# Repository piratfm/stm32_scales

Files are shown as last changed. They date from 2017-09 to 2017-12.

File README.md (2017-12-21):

# STM32 scales

Software and hardware for child weight meter (scales) with glass LCD display
Based on branded Chicco weight meter model # 8312.60.001

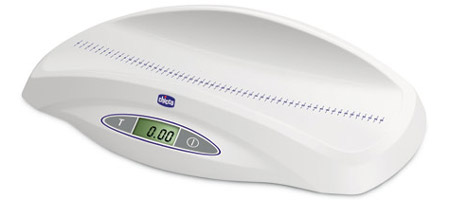
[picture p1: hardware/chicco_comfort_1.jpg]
scales image


Due original "brains" PCB became broken for some reason (operational amplifier burned-out, and scales always shows zeroes), the decision to replace
it by STM32 is made. As additional "pro", scales precision has been 10x increased, comparing to original "brains" of scales.

## Original parts that been used:
 * load sensors bridge (3 pins each).
 * original 5 symbol glass LCD display.
 * original plastic enclosure with pushbuttons.

## Used hardware:
 * HX711 ADC
 * STM32F103C8T6 as MCU and software-base LCD controller (by using RTC interrupts)
 
 schematic of the board: [schematic](https://github.com/piratfm/stm32_scales/blob/master/hardware/weightmeter_schematic.pdf)

## To calibrate:
 1. Put weight meter into the flat table (without any load).
 2. Press "tare" button when powering-on device (press both buttons, tare and power).
 3. You will see some 5-digit number, this is initial ADC value without scale.
 4. When You see "10.000" on display, put 10.000 Kg reference load onto weight meter.
 5. You will see some 5-digit number again, but a little bit higher, this is ADC value with load and without scale.
 6. Then You will see 4-digit number in range 35...300. This is calculated "scale" value for calibration, that number will be saved into flash.
 7. Done, Your weight meter is now calibrated and displays correct value in Kg.

## To measure:
 1. Turn on scales.
 2. Wait until it shows 00000.
 3. Put load into the scales and wait until triangle appears on display.
 4. There will be actual measured weight (in average mode), so even if kid is moving, the scales are still show precise value.
 5. After some time, the weight amount will blink and keeps displayed even if load is removed (memory function).
 6. After some time more, scales turns off automatically.

## Power consumption:
Active mode: 6 mA
Power down mode: 20 uA

License: GPL

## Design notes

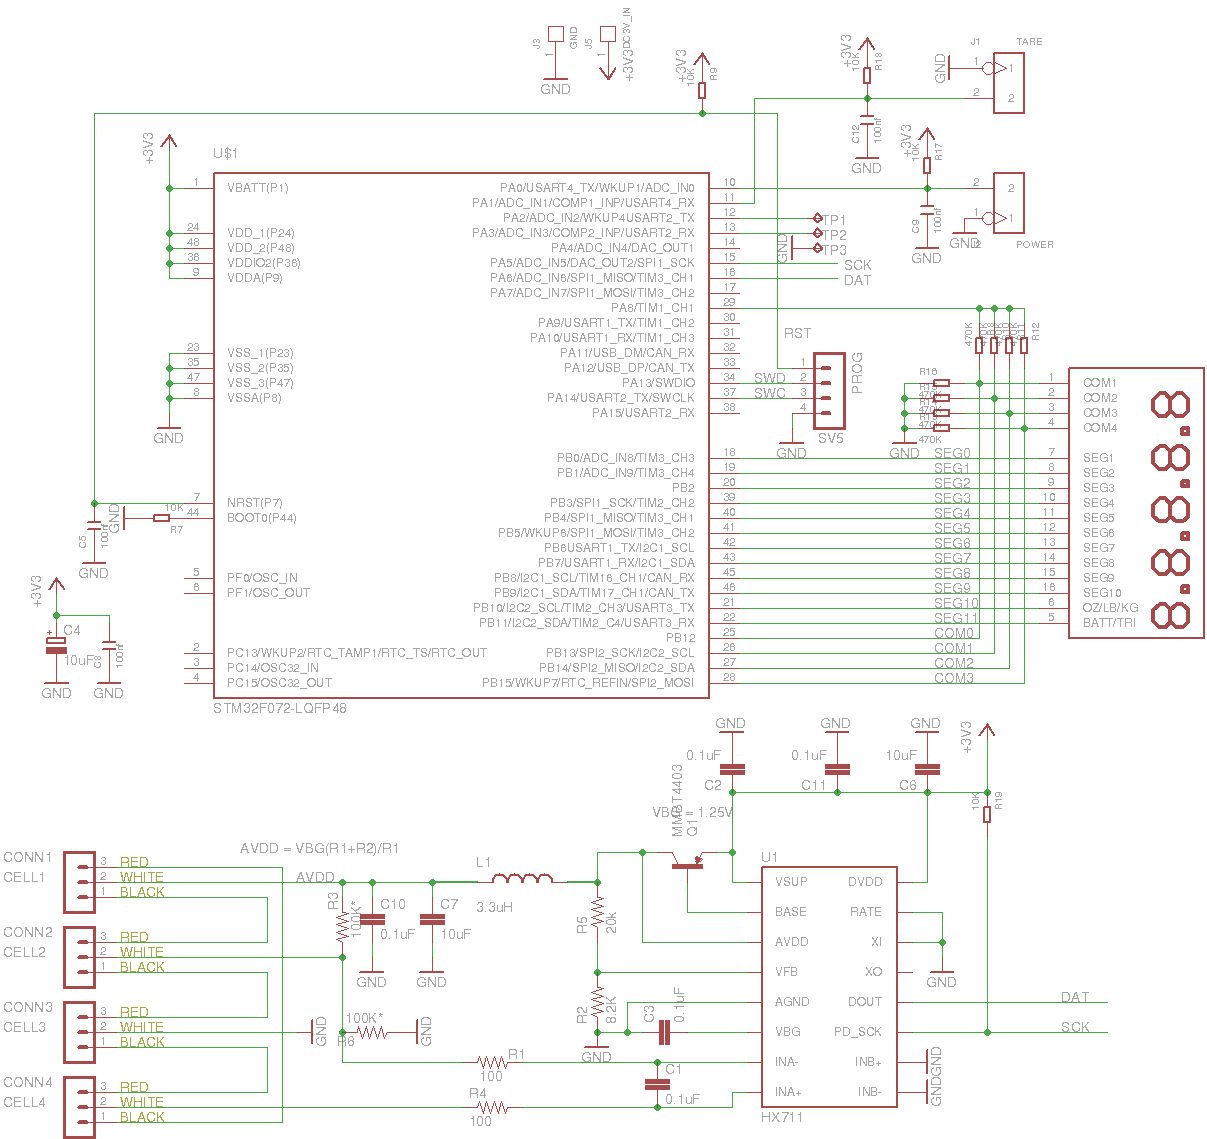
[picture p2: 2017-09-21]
hardware/schematic.png

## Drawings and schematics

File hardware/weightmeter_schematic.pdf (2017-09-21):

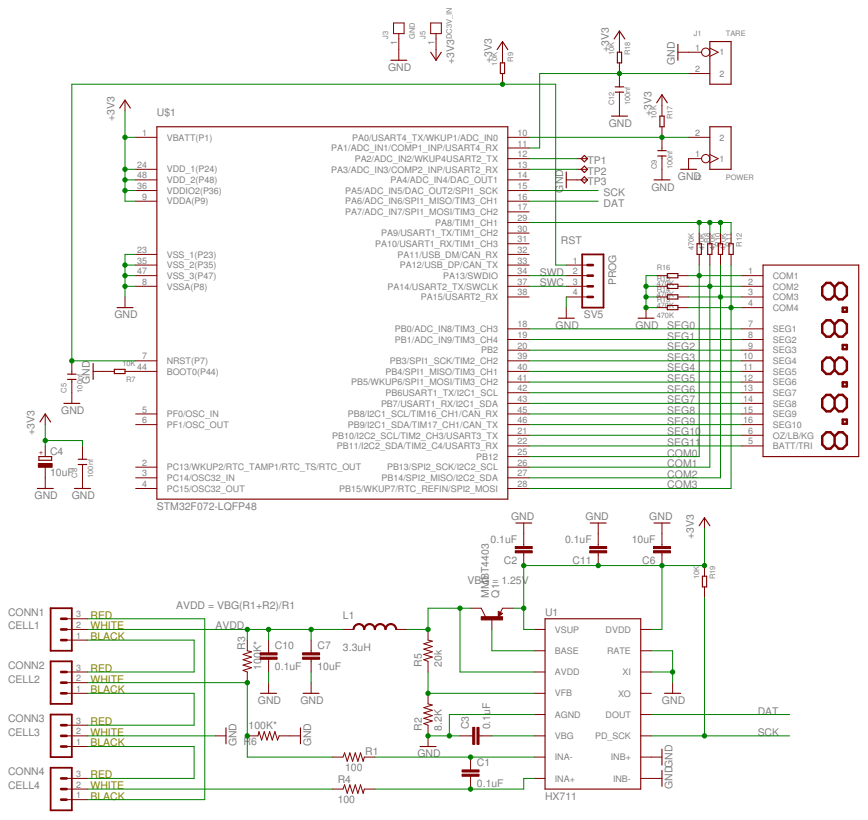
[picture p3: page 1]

VDDIO2(P36) 36 | 15 PA6/ADC_IN6/SPI1_MISO/TIM3_CH1
VDDA(P9) 9 | 16 PA7/ADC_IN7/SPI1_MOSI/TIM3_CH2
VSS_1(P23) 23 | 17

46 SEG9 | 16

21 PB11/I2C2_SDA/TIM2_C4/USART3_RX SEG10

22 SEG11

25 PB13/SPI2_SCK/I2C2_SCL COM0

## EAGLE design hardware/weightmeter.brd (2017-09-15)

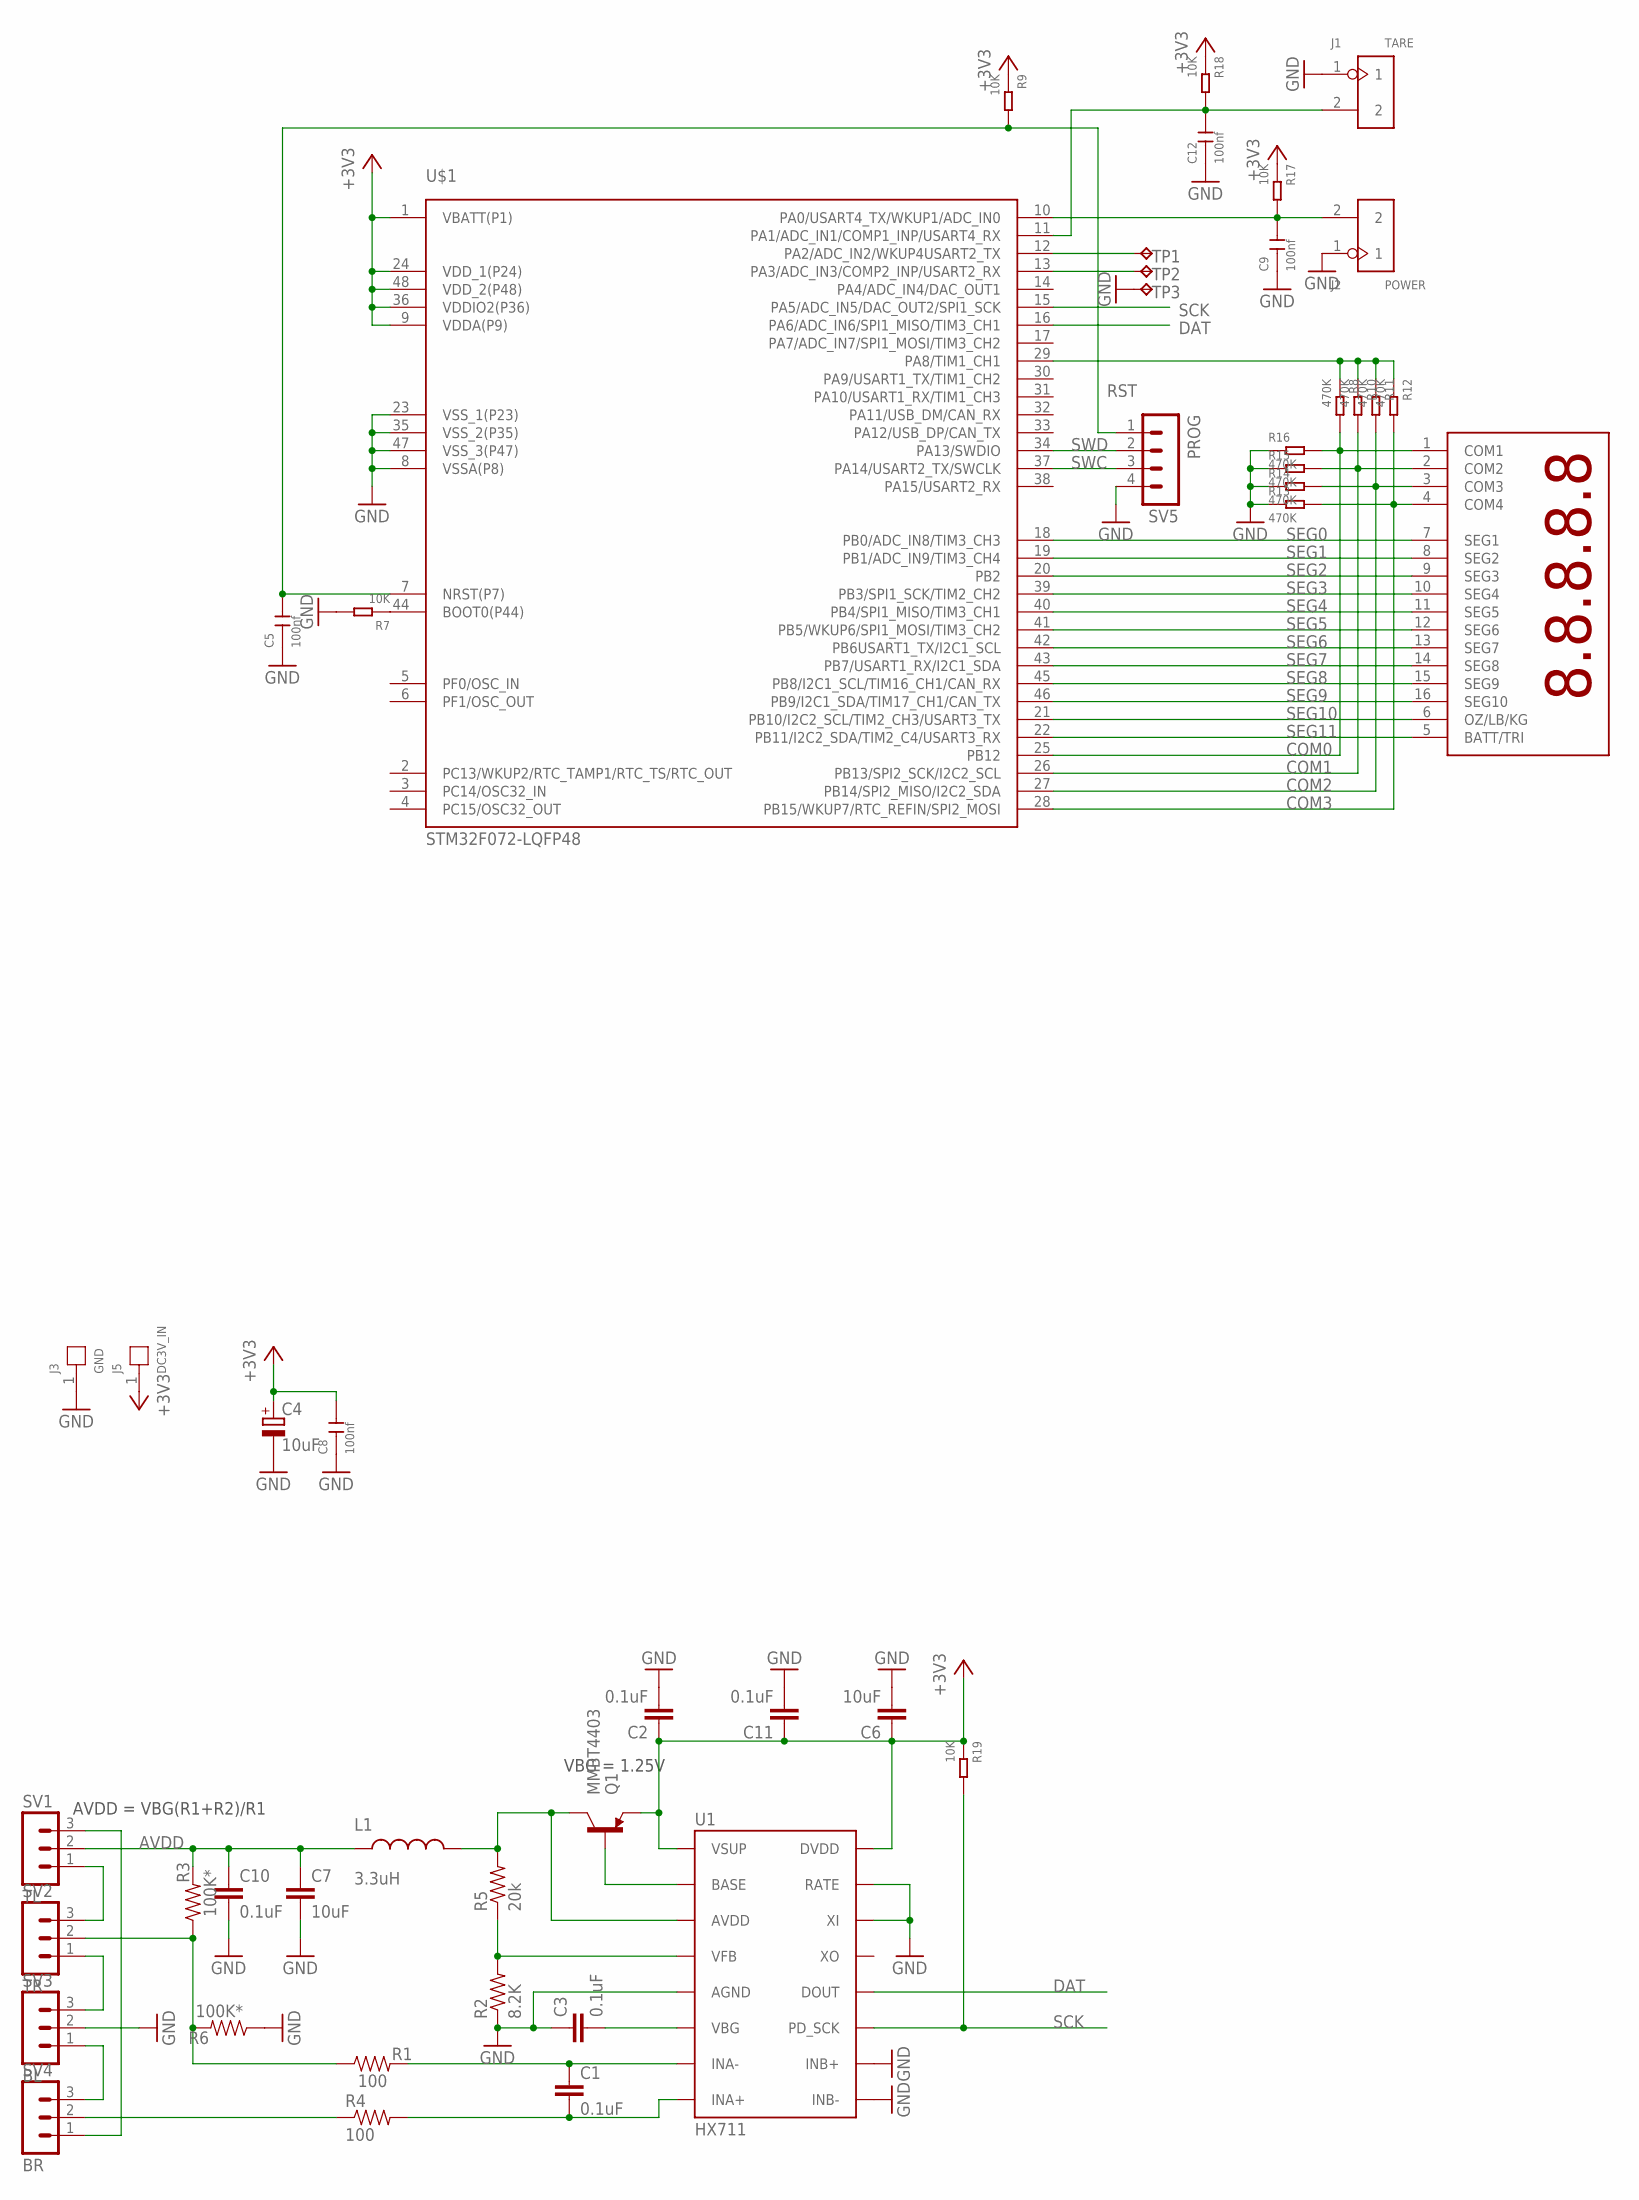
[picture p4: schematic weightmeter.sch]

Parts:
C1, C2, C3, C10, C11: 0.1uF; 0603-CAP
C4: 10uF; A/3216-18R
C5, C8, C9, C12: 100nf; C0805
C6, C7: 10uF; 1210
J1: TARE; H2-2.54
J2: POWER; H2-2.54
J3: GND; 1P-65/35MIL
J5: DC3V_IN; 1P-65/35MIL
L1: 3.3uH; 0805
Q1: MMBT4403; SOT23-3
R1, R4: 100; 0603-RES
R2: 8.2K; 0603-RES
R3, R6: 100K*; 0603-RES
R5: 20k; 0603-RES
R7, R9, R17, R18, R19: 10K; R0805
R8, R10, R11, R12, R13, R14, R15, R16: 470K; R0805
SV1: TL; MA03-1
SV2: TR; MA03-1
SV3: BL; MA03-1
SV4: BR; MA03-1
SV5: PROG; MA04-1
TP1, TP2, TP3: UART_OUT; B1,27
U1: HX711; SO16
U$1: STM32F072-LQFP48; LQFP48
X1: 1296-T08; 1296-08

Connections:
+3V3: C2.1, C4.+, C6.1, C8.2, C11.1, J5.1, Q1.2 (E), R9.1, R17.1, R18.1, R19.1, U1.1 (VSUP), U1.16 (DVDD), U$1.1 (VBATT(P1)), U$1.9 (VDDA(P9)), U$1.24 (VDD_1(P24)), U$1.36 (VDDIO2(P36)), U$1.48 (VDD_2(P48))
A+: R4.1, SV4.2
A-: R1.1, R3.1, R6.2, SV2.2
AVDD: C7.1, C10.1, L1.1, R3.2, SV1.2
COM0: R8.2, R16.2, U$1.25 (PB12), X1.1 (COM1)
COM1: R10.2, R15.2, U$1.26 (PB13/SPI2_SCK/I2C2_SCL), X1.2 (COM2)
COM2: R11.2, R14.2, U$1.27 (PB14/SPI2_MISO/I2C2_SDA), X1.3 (COM3)
COM3: R12.2, R13.2, U$1.28 (PB15/WKUP7/RTC_REFIN/SPI2_MOSI), X1.4 (COM4)
DAT: U1.12 (DOUT), U$1.16 (PA6/ADC_IN6/SPI1_MISO/TIM3_CH1)
GND: C2.2, C3.1, C4.-, C5.1, C6.2, C7.2, C8.1, C9.1, C10.2, C11.2, C12.1, J1.1, J2.1, J3.1, R2.1, R6.1, R7.2, R13.1, R14.1, R15.1, R16.1, SV3.2, SV5.4, TP3.TP, U1.5 (AGND), U1.9 (INB-), U1.10 (INB+), U1.14 (XI), U1.15 (RATE), U$1.8 (VSSA(P8)), U$1.23 (VSS_1(P23)), U$1.35 (VSS_2(P35)), U$1.47 (VSS_3(P47))
unnamed: SV1.1, SV2.3
unnamed: SV2.1, SV3.3
unnamed: SV3.1, SV4.3
unnamed: SV1.3, SV4.1
unnamed: Q1.1 (B), U1.2 (BASE)
unnamed: R2.2, R5.1, U1.4 (VFB)
unnamed: C3.2, U1.6 (VBG)
unnamed: L1.2, Q1.3 (C), R5.2, U1.3 (AVDD)
unnamed: TP1.TP, U$1.12 (PA2/ADC_IN2/WKUP4USART2_TX)
unnamed: C1.1, R1.2, U1.7 (INA-)
unnamed: C1.2, R4.2, U1.8 (INA+)
unnamed: TP2.TP, U$1.13 (PA3/ADC_IN3/COMP2_INP/USART2_RX)
unnamed: C12.2, J1.2, R18.2, U$1.11 (PA1/ADC_IN1/COMP1_INP/USART4_RX)
unnamed: R7.1, U$1.44 (BOOT0(P44))
unnamed: C9.2, J2.2, R17.2, U$1.10 (PA0/USART4_TX/WKUP1/ADC_IN0)
unnamed: R8.1, R10.1, R11.1, R12.1, U$1.29 (PA8/TIM1_CH1)
RST: C5.2, R9.2, SV5.1, U$1.7 (NRST(P7))
SCK: R19.2, U1.11 (PD_SCK), U$1.15 (PA5/ADC_IN5/DAC_OUT2/SPI1_SCK)
SEG0: U$1.18 (PB0/ADC_IN8/TIM3_CH3), X1.7 (SEG1)
SEG1: U$1.19 (PB1/ADC_IN9/TIM3_CH4), X1.8 (SEG2)
SEG2: U$1.20 (PB2), X1.9 (SEG3)
SEG3: U$1.39 (PB3/SPI1_SCK/TIM2_CH2), X1.10 (SEG4)
SEG4: U$1.40 (PB4/SPI1_MISO/TIM3_CH1), X1.11 (SEG5)
SEG5: U$1.41 (PB5/WKUP6/SPI1_MOSI/TIM3_CH2), X1.12 (SEG6)
SEG6: U$1.42 (PB6USART1_TX/I2C1_SCL), X1.13 (SEG7)
SEG7: U$1.43 (PB7/USART1_RX/I2C1_SDA), X1.14 (SEG8)
SEG8: U$1.45 (PB8/I2C1_SCL/TIM16_CH1/CAN_RX), X1.15 (SEG9)
SEG9: U$1.46 (PB9/I2C1_SDA/TIM17_CH1/CAN_TX), X1.16 (SEG10)
SEG10: U$1.21 (PB10/I2C2_SCL/TIM2_CH3/USART3_TX), X1.6 (OZ/LB/KG)
SEG11: U$1.22 (PB11/I2C2_SDA/TIM2_C4/USART3_RX), X1.5 (BATT/TRI)
SWC: SV5.3, U$1.37 (PA14/USART2_TX/SWCLK)
SWD: SV5.2, U$1.34 (PA13/SWDIO)

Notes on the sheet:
VBG = 1.25V
AVDD = VBG(R1+R2)/R1

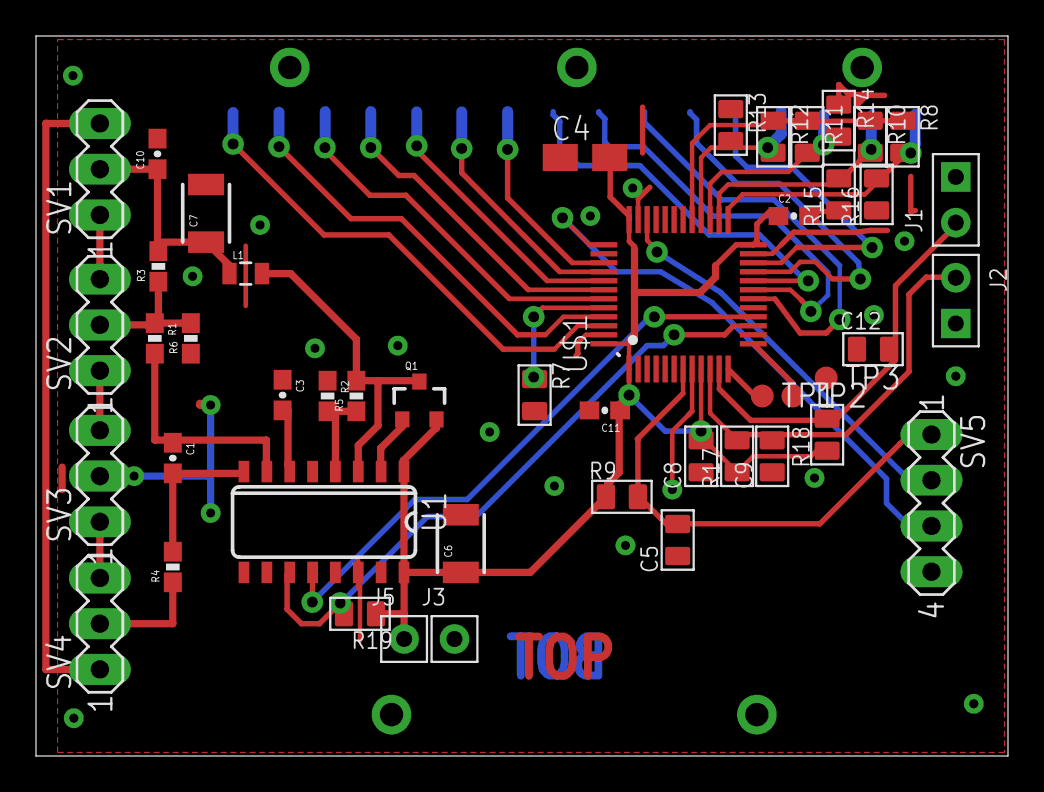
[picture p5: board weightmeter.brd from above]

Board: 2 copper layers, 54.0 x 40.0 mm, 48 parts (1 on the bottom side), 42 nets.

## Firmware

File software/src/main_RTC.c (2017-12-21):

/**
  ******************************************************************************
  * @file GlassLCD/src//main_RTC.c 
  * @author  MCD Application Team
  * @version  V2.0.0
  * @date  04/27/2009
  * @brief  Main program body using RTC method and STOP mode
  ******************************************************************************
  * @copy
  *
  * THE PRESENT FIRMWARE WHICH IS FOR GUIDANCE ONLY AIMS AT PROVIDING CUSTOMERS
  * WITH CODING INFORMATION REGARDING THEIR PRODUCTS IN ORDER FOR THEM TO SAVE
  * TIME. AS A RESULT, STMICROELECTRONICS SHALL NOT BE HELD LIABLE FOR ANY
  * DIRECT, INDIRECT OR CONSEQUENTIAL DAMAGES WITH RESPECT TO ANY CLAIMS ARISING
  * FROM THE CONTENT OF SUCH FIRMWARE AND/OR THE USE MADE BY CUSTOMERS OF THE
  * CODING INFORMATION CONTAINED HEREIN IN CONNECTION WITH THEIR PRODUCTS.
  *
  * <h2><center>&copy; COPYRIGHT 2009 STMicroelectronics</center></h2>
  */ 


/* Includes ------------------------------------------------------------------*/
#include "stm32f10x.h"
#include "SystemConfig_RTC.h"
#include "hx711.h"
#include <math.h>


/** @addtogroup GlassLCD
  * @{
  */ 


/* Private typedef -----------------------------------------------------------*/
/* Private define ------------------------------------------------------------*/
/* Private macro -------------------------------------------------------------*/
/* Private variables ---------------------------------------------------------*/
/* Private function prototypes -----------------------------------------------*/
/* Private functions ---------------------------------------------------------*/ 

extern uint16_t  SegmentsValues_Lower_Quarter_Digits[4];
extern __IO uint32_t LCDPowerOn;
extern __IO uint32_t TarePressed;
extern __IO uint32_t VoltageFlag;

void __cxa_pure_virtual(void) {Error_Handler();}
void __cxa_deleted_virtual(void) {Error_Handler();}

#ifdef DEBUG_TO_UART
int _write(int file, char *data, int len) {
	int i;
	for(i=0;i<len;i++) {
		USART_SendData(USART2, data[i]);
		while (USART_GetFlagStatus(USART2, USART_FLAG_TC) == RESET) {}
	}
	return len;
}
int _write_r (struct _reent *r, int file, char * ptr, int len) {
	int i;
	for(i=0;i<len;i++) {
		USART_SendData(USART2, ptr[i]);
		while (USART_GetFlagStatus(USART2, USART_FLAG_TC) == RESET) {}
	}
	return len;
}
#endif
#define printf(x,...)

void Delay(int val) {
	__IO uint32_t i = val;
	for(; i != 0; i--)
	{
	}
}

typedef union {
  float    f;
  uint32_t u;
} sc_t;

#define DEFAULT_SCALE 70.0
/**
  * @brief  Main program.
  * @param  None
  * @retval : None
  */
int main(void)
{
  int cnt_raw = 0;
  int prev_value = 0;
  int prev_value_count = 0;
  int tare = 0;
  int i;
  int is_intial = 1;
  int is_tare_setted = 0;

  double val_buffer[32];
  int val_filled = 0;
  double val;



  LCDPowerOn=0;

  sc_t scale;
  scale.f = DEFAULT_SCALE;
  /* System configuration */
  SystemConfiguration();
  GPIO_SetBits(LCD_Bias_Port, LCD_BiasPlus_Pin);

do_calc_scale:
  if(GPIO_ReadInputDataBit(GPIOA, GPIO_Pin_1) == Bit_RESET) {
	 LCDPowerOn=2;
	 LCD_WriteCfg();
	 cnt_raw = HX711_Average_Value(1, 8);
	 printf("do configuration!\r\n");
	 while(GPIO_ReadInputDataBit(GPIOA, GPIO_Pin_1) == Bit_RESET) {}

	 VoltageFlag = (PWR_GetFlagStatus(PWR_FLAG_PVDO)==SET) ? 0x800 : 0x000;
	 if(VoltageFlag)
		 goto measures_begin;
	 //TODO: do configuration!
     printf("Calculating scale...\r\n");
     Delay(500000);
     printf("Getting zero weight....\r\n");
     cnt_raw = HX711_Average_Value(1, 32);
     printf("cnt[0.000]: %d => %d\r\n", cnt_raw);
     LCD_WriteInt(cnt_raw/100, 0);
     printf("Now put 10.000Kg and measure weight again...\r\n");
     Delay(500000);
     for (i=0;i<10;i++) {
    	 LCD_WriteNone();
    	 Delay(60000);
    	 LCD_WriteInt(10000, 0);
    	 Delay(60000);
     }
     tare = HX711_Average_Value(1, 32);
     printf("cnt[10.000]: %d\r\n", tare);
     LCD_WriteInt(tare/100, 0);
     Delay(1000000);
     double scale2 = ((double)((double)tare - (double)cnt_raw)) / 10000.0;
     scale.f = scale2;
     if(scale.f < 0)
    	 scale.f = -scale.f;
     printf("scale[1/10.000]: %d\r\n", (int)scale.f);
     LCD_WriteInt(scale.f, 0);
     Delay(500000);

     if(scale.f < 35.0 || scale.f > 250.0) {
    	 printf("scale is too bad: %d!\r\n", (int)scale.f);
         for (i=0;i<10;i++) {
        	 LCD_WriteCfg();
        	 Delay(50000);
        	 LCD_WriteNone();
        	 LCD_WriteError();
        	 Delay(50000);
         }
    	 scale.f=DEFAULT_SCALE;
     } else {
         FLASH_Unlock();
         FLASH_ClearFlag(FLASH_FLAG_BSY | FLASH_FLAG_EOP | FLASH_FLAG_PGERR | FLASH_FLAG_WRPRTERR);
    	 FLASH_ErasePage(0x800FC00);
         FLASH_ProgramWord(0x800FC04, 0xa5a5a5a5);
         FLASH_ProgramWord(0x800FC08, scale.u);
         FLASH_Lock();
         printf("Done, scale saved!\r\n");
     }
  } else {
	  uint32_t *scale_sign_u32 =  (uint32_t*)0x800FC04;
	  uint32_t *scale_u32 =  (uint32_t*)0x800FC08;
	  if(*scale_sign_u32 != 0xa5a5a5a5) {
		  scale.f = DEFAULT_SCALE;
		  printf("scale is unknown! needs fixing (%d != %d)!\r\n", *scale_sign_u32, 0xa5a5a5a5);
		  LCD_WriteLines();
		  Delay(1000000);
	  } else {
		  //scale = *scale_u32;
		  uint32_t scale_u = *scale_u32;
		  scale.u = scale_u;
		  printf("scale is: %u\r\n", (uint32_t) (*scale_u32));
		  if(scale.u == 0xFFFFFFFF || scale.f == 0.0) {
			  scale.f = DEFAULT_SCALE;
			  printf("scale is bad value! needs fixing!\r\n");
			  LCD_WriteLines();
			  Delay(1000000);
		  } else {
			  LCD_WriteAll();
		  }
	  }
  }

measures_begin:
  /* Power on the resistor bridge */
LCDPowerOn=1;

  is_intial = 1;
  is_tare_setted = 0;
  val_filled = 0;
  val = 0.0;

  printf("Hello main! Scale is: %d\r\n", scale);
  TarePressed=0;

  while(1) {
	VoltageFlag = (PWR_GetFlagStatus(PWR_FLAG_PVDO)==SET) ? 0x800 : 0x000;
	  //read data....
#if 1
	if(!LCDPowerOn) {
re_sleep:
		printf("Powering off...\r\n");
		while(GPIO_ReadInputDataBit(GPIOA, GPIO_Pin_0) == Bit_RESET) {};
		Delay(50000);
		/* Request to enter STOP mode with regulator low power */
#if 1
		GPIO_InitTypeDef GPIO_InitStructure;
		  GPIO_InitStructure.GPIO_Pin = GPIO_Pin_All;
		  GPIO_InitStructure.GPIO_Mode = GPIO_Mode_AIN;
		  GPIO_Init(GPIOA, &GPIO_InitStructure);
		  GPIO_Init(GPIOB, &GPIO_InitStructure);
		  GPIO_Init(GPIOC, &GPIO_InitStructure);

//		  GPIO_InitStructure.GPIO_Pin = GPIO_Pin_2|GPIO_Pin_3|GPIO_Pin_4|GPIO_Pin_6|GPIO_Pin_7|GPIO_Pin_8|
//				                   GPIO_Pin_9|GPIO_Pin_10|GPIO_Pin_11|GPIO_Pin_12|GPIO_Pin_13|GPIO_Pin_14|GPIO_Pin_15;
//		  GPIO_InitStructure.GPIO_Mode = GPIO_Mode_AIN;
//		  GPIO_Init(GPIOA, &GPIO_InitStructure);
#endif
		Delay(5000);

	    TarePressed=0;
		//PWR_EnterSTOPMode(PWR_Regulator_LowPower, PWR_STOPEntry_WFI);

		//GPIO_Configuration();
	    PWR_WakeUpPinCmd(ENABLE);
		Delay(5000);
		PWR_EnterSTANDBYMode();
		Delay(5000);
		//tune scale
		if(GPIO_ReadInputDataBit(GPIOA, GPIO_Pin_0) == Bit_RESET && GPIO_ReadInputDataBit(GPIOA, GPIO_Pin_1) == Bit_RESET)
			goto do_calc_scale;

		if(GPIO_ReadInputDataBit(GPIOA, GPIO_Pin_0) != Bit_RESET)
			goto re_sleep;

		Delay(5000);
		continue;
        //RCC->APB1ENR |= RCC_APB1ENR_PWREN;
        //SCB->SCR |= SCB_SCR_SLEEPDEEP;
        //PWR->CR |= PWR_CR_PDDS;
        //PWR->CR |= PWR_CR_CWUF;
        //PWR->CSR |= PWR_CSR_EWUP;
        //__WFE();
	}
#endif

	cnt_raw = HX711_Average_Value(1, 8);
	printf("cnt: %d => %d, LCD: %d\r\n", cnt_raw, cnt_raw - tare, (cnt_raw - tare)/scale);

	if(is_intial) {
		is_intial=0;
		continue;
	} else if (is_tare_setted) {
		int val_int = cnt_raw - tare;
		double val_new = ((double)val_int)/((double)scale.f);
		val_buffer[val_filled & 0x1f] = val_new;
		val_filled++;
		if(val_filled < 48) {
			//reset counters if too large difference (+/-250 grams)
			double val_diff = val_new - val;
			if(val_diff > 250.0 || val_diff < -250.0 || val_new < 500.0)
				val_filled=0;
			if(val_filled < 32) {
				val = val_new;
			} else {
				int arr_cnt;
				val=0.0;
				for(arr_cnt=0;arr_cnt<32;arr_cnt++) {
					val += val_buffer[arr_cnt];
				}
				val = val/32.0;
			}
			LCD_WriteInt(val, (val_filled >= 32));
		} else {
			for (i=0;i<10;i++) {
				LCD_WriteNone();
				Delay(100000);
				LCD_WriteInt(val, 1);
				Delay(100000);
			}
			val_filled=0;
			//don't measure, just display.
			Delay(10000000);
			goto re_sleep;
		}
	} else {
		tare=cnt_raw;
		printf("new tare: %d\r\n", tare);
		is_tare_setted=1;
	}

	if(TarePressed==1 && GPIO_ReadInputDataBit(GPIOA, GPIO_Pin_1) == Bit_SET) {
		printf("Set tare next time!\r\n");
		Delay(50000);
		is_tare_setted=0;
		TarePressed=0;
	}

	//if same weight for a long time, go to sleep...
	if(cnt_raw/1000 != prev_value) {
		prev_value=cnt_raw/1000;
		prev_value_count=0;
	} else {

		prev_value_count++;

		if(prev_value_count >= 256)
			goto re_sleep;
	}

  }

}


#ifdef USE_FULL_ASSERT


/**
  * @brief  Reports the name of the source file and the source line number
  * where the assert_param error has occurred.
  * @param file: pointer to the source file name
  * @param line: assert_param error line source number
  * @retval : None
  */
void assert_failed(uint8_t* file, uint32_t line)
{ 
  /* User can add his own implementation to report the file name and line number,
     ex: printf("Wrong parameters value: file %s on line %d\r\n", file, line) */

  /* Infinite loop */
  while (1)
  {
  }
}
#endif

/**
  * @}
  */ 



/******************* (C) COPYRIGHT 2009 STMicroelectronics *****END OF FILE****/

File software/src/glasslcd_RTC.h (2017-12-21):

/**
  ******************************************************************************
  * @file GlassLCD/inc/glasslcd_RTC.h 
  * @author  MCD Application Team
  * @version  V2.0.0
  * @date  04/27/2009
  * @brief  LCD glass configuration header file for RTC method.
  ******************************************************************************
  * @copy
  *
  * THE PRESENT FIRMWARE WHICH IS FOR GUIDANCE ONLY AIMS AT PROVIDING CUSTOMERS
  * WITH CODING INFORMATION REGARDING THEIR PRODUCTS IN ORDER FOR THEM TO SAVE
  * TIME. AS A RESULT, STMICROELECTRONICS SHALL NOT BE HELD LIABLE FOR ANY
  * DIRECT, INDIRECT OR CONSEQUENTIAL DAMAGES WITH RESPECT TO ANY CLAIMS ARISING
  * FROM THE CONTENT OF SUCH FIRMWARE AND/OR THE USE MADE BY CUSTOMERS OF THE
  * CODING INFORMATION CONTAINED HEREIN IN CONNECTION WITH THEIR PRODUCTS.
  *
  * <h2><center>&copy; COPYRIGHT 2009 STMicroelectronics</center></h2>
  */ 


/* Define to prevent recursive inclusion -------------------------------------*/
#ifndef __GLASSLCD_RTC_H
#define __GLASSLCD_RTC_H

/* Includes ------------------------------------------------------------------*/
#include "stm32f10x.h"
#include "SystemConfig_RTC.h"

/* Exported constants --------------------------------------------------------*/

/*----------------------- LCD user configuration -----------------------------*/
/* Incomment the define line of the used LCD and comment the other one */
//#define USE_LCD_REF_PD_878    /* LCD ref: PD_878 : 8 digits 128 segments */
#define USE_LCD_REF_CT4_098  /* LCD ref: CT4-098: 4 digits 64 segments */

/* Common lines configuration ----------------------------------------------- */
#define CommonLines_Port   GPIOB /* Port where the 4 common lines are connected */

#define CommonLines_EightHighPortPins  
                                /*  The previous line is to define where Common
                                    lines are located:
                                    - Uncomment this line: the 4 common lines  
                                      are located between PX.8 and PX.15
                                    - Comment this line: the 4 common lines  
                                      are located between PX.0 and PX.7
                                */

#define CommonLines_Pin_Offset   4   /* Pin offset (do not exceed 4: [0..4]) 
                                       (offset of eight low port pins or
                                       eight high port pins according to
                                       CommonLines_EightHighPortPins commented
                                       or not */

/* Configuration of the two GPIOs which drive the LCD (power on/off) -------- */
#define LCD_Bias_Port        GPIOA /* Port which the LCD bias plus pins are connected */


#define LCD_BiasPlus_Pin     GPIO_Pin_8  /* The number of the first GPIO (LCD bias plus)   
                                            wich will power-off the resistor bridge in 
                                            low power mode */

/* Segment lines configuration ---------------------------------------------- */
/* Port where the Low Quarter digits segment lines are connected */
#define SegmentsLines_LQD_Port   GPIOB  

/* Enable the used GPIOs clocks */
#define RCC_APB2Periph_Used_GPIO    RCC_APB2Periph_GPIOB|RCC_APB2Periph_GPIOA

/* LCD interrupt priority configuration ------------------------------------- */
#define LCD_Priority_Value       1

/* If the LCD interrupt is run always as priority 0 please comment this line */
#define LCD_Use_Boost_Priority 

/* LCD Contrast value settings */
/* LCDContrastValue and PeriodValue are the only parameters modifiable by the user */
#define LCDContrastValue          70  /* LCD Contrast value in percent from 0 to 100 */
#define PeriodValue               28  /* Period */

/* Parameters not modifiable by the user */
#define PulseValueForContrast     ((LCDContrastValue * PeriodValue) / 100)
#define DeadTimeValue             (PeriodValue - PulseValueForContrast)
#define PulseValueForContrastLow  (PulseValueForContrast & (uint32_t)0x0000FFFF)
#define PulseValueForContrastHigh ((PulseValueForContrast & (uint32_t)0xFFFF0000) >> 16)
#define DeadTimeValueLow          (DeadTimeValue & (uint32_t)0x0000FFFF)
#define DeadTimeValueHigh         ((DeadTimeValue & (uint32_t)0xFFFF0000) >> 16)

/*------ GPIOs Masks definitions (section not modifiable by the user) --------*/
#define PinsConfig         CRH
#define ALL_COMMON_LINES  (uint16_t)(0xF000)

#define ALL_COMMON_LINES_PP   (0x33330000)

#define ALL_SEGMENT_LINES      0x0FFF
//#define ALL_SEGMENT_LINES_PP   0x33333333
#define ALL_SEGMENT_LINES_PP   0x33333333


/* Exported types ------------------------------------------------------------*/
/* Exported macro ------------------------------------------------------------*/
/* Exported functions ------------------------------------------------------- */
/* APPLICATION LAYER ---------------------------------------------------------*/
void LCD_GPIO_Init(void);
void LCD_WriteInt(int val, int flag);
void LCD_WriteLines();
void LCD_WriteNone();
void LCD_WriteAll();
void LCD_WriteCfg();
void LCD_WriteError();

#endif /* __GLASSLCD_RTC_H */

/******************* (C) COPYRIGHT 2009 STMicroelectronics *****END OF FILE****/

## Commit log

2017-09-15 initial release. Fix minimal scale to 35.
    [weightmeter.brd, weightmeter.sch]
2017-09-19 fix power off. Higher gain.

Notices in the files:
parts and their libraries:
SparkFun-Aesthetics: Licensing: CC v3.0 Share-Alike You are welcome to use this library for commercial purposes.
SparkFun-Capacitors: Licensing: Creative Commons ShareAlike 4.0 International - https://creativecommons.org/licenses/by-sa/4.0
